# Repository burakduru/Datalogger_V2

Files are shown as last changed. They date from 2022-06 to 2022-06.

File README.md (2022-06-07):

# Datalogger_V2
    

__Ce répertoire Github regroupe la partie électronique et informatique embarquée de la carte d'acquistion Datalogger_V2 rédigé par Burak DURU en tant qu'apprenti ingénieur en électronique à la [Division Technique de l'INSU Meudon](https://www.dt.insu.cnrs.fr/).__

## Carte d'acquisition 

Réalisation et mise en œuvre d'une carte d'acquisition avec un microcontrôleur [Teensy 3.6](https://www.pjrc.com/store/teensy36.html) dans le but de recevoir/traiter des valeurs de thermistances/résistances chauffantes et transmettre/reçevoir des informations via plusieurs mode de communications

Fonctionnalités de la carte d’acquisition :
* Microcontrôleur [Teensy 3.6](https://www.pjrc.com/store/teensy36.html) :
  * Processeur 32 bits: Cortex-M4 @ 180 MHz 
  * Mémoires: 1M Flash, 256K RAM et 4K EEPROM
  * Microcontrôleur MK66FX1M0VMD18
  * Port USB High Speed (480 Mbit/sec)
  * 2 port Bus CAN
  * 22 sorties PWM
  * 4 ports I2C
  * 62 broches E/S (dont 48 format DIL compatible breadboard - non tolérante au +5 V). Les entrées/sorties fonctionnent en 3.3 V 
  * 25 entrées analogiques (à 2 ADC résolution 13 bits)
  * 2 sorties analogiques (DAC résolution 12 bits)
  * Port USB Full Speed (12 Mbit/sec)
  * Ethernet jusqu'à 100 Mbits/sec
  * Port intégré (4-bit SDIO) pour carte microSD™ (carte non livrée)
  * Port Audio numérique I2S, 4 canaux Entrée & Sortie
  * 14 Timers Hardware
  * 3 ports SPI (dont 1 avec FIFO)
  * 6 port série (dont 2 FIFO et Baud Rates rapides)
  * Horloge temps réelle
  * Dimensions: 62,3 x 18 x 4,2 mm

  teensy3 6
 
* [Socket MikroBUS](https://www.mikroe.com/mikrobus/) pour l’utilisation des modules “Click”
* Ethernet ([Module WIZ820-IO](https://www.wiznet.io/product-item/wiz820io/))
* Sortie DAC, GPIO et commande Interlock Laser
* Bus CAN
* Liaison RS232
* Connectique pour le réseau de thermistances/tensions
* Alimentation externe
* Relais

datalogger_v2_3D

## Programmes utilisés

* __[Datalogger](https://github.com/burakduru/dataloggerv2/blob/main/Programmes/microdial_datalogger_V2/microdial_datalogger_V2.ino)__ : *Permettant de récupérer les informations de températures et de tensions des connectiques thermistances YSI[...] et de tensions V[...] via une transmission RS232*  
* __[Bus CAN](https://github.com/burakduru/dataloggerv2/blob/main/Programmes/bus_can/bus_can.ino)__ : *Permettant de recevoir/transmettre des trames de données depuis le bus de donnée CAN. (Dans notre exemple, transmission d’une donnée de compteur et de thermistances)*
* __[Ethernet](https://github.com/burakduru/dataloggerv2/blob/main/Programmes/wiz820io_mqtt_ethernet/wiz820io_mqtt_ethernet.ino)__ : *Programme d’exemples pour l’initialisation module Ethernet / Envoi et réception de trames UDP / Connexion à un broker MQTT et le statut de connexion* 
* __[Programmes de tests](https://github.com/burakduru/dataloggerv2/tree/main/Programmes/click_exemples)__ : *Modules “Click” utilisés*
* __[WIFI](https://github.com/burakduru/dataloggerv2/blob/main/Programmes/adafruitio_wifi/adafruit_io_wifi_mqtt_16_04.ino)__ : *Programme pour le scan/connexion des réseaux et connexion à un serveur/broker MQTT* 
* __[LoRa](https://github.com/burakduru/dataloggerv2/blob/main/Programmes/LoRa_microdial_send_temp/LoRa_microdial_send_temp.ino)__ : *Plusieurs programmes permettant d’initialiser et d’envoyer des trames de données via le protocol de communication bas débit LoRa* 
* __[AdafruitIO | ThinkSpeak](https://github.com/burakduru/dataloggerv2/tree/main/Programmes)__ : *Envoi/réception de données en utilisant une connexion Internet (via Ethernet ou WIFI) à un serveur MQTT* 

## Matériel

* __[PCB](https://github.com/burakduru/dataloggerv2/tree/main/PCB)__: *Fichiers schématique (.schDoc) et PCB (.pcbDoc) sous Altium Designer*

## Schéma fonctionnement complet

* __[Schématique](https://github.com/burakduru/dataloggerv2/blob/main/MicroDial_Data_Log_V2_SCH.pdf)__ : *Fichier PDF regroupant la schématique de la carte* d'acquisition Datalogger_V2

Guide d'utilisation 
===================

<!--ts-->
* [Installation de Teensyduino](#installation-de-teensyduino)    
* [Installation de bibliothèques sous Teensyduino](#installation-de-bibliothèques-sous-teensyduino)  
* [Modules Click Board](#modules-click-board)
* [Pinout DataloggerV2](#pinout-dataloggerV2)
* [Liaison RS232](#liaison-rs232)
* [Visual Studio](#visual-studio) 
* [Bus CAN](#bus-can)  
* [Ethernet](#ethernet)  
* [WIFI](#wifi)
* [AdafruitIO](#adafruitio) 
* [Thingspeak](#thingspeak)
* [LoRa](#lora)  
* [Bluetooth Low Energy](#bluetooth-low-energy)
<!--te-->

Installation de Teensyduino
---------------------------

Télécharger l’Add-On pour l’IDE d’Arduino en utilisant ce lien sous Windows: https://www.pjrc.com/teensy/td_download.html.
Avec Windows 10, il n’y a pas de driver à installer : On choisit donc, le chemin d’accès où se trouve arduino.exe : 

teensyduino1

Choisir comme type de carte sur Arduino :
Teensy 3.6 / USB Type : “Serial” / CPU Speed : “180MHz” / Port : “Numéro de Port du Teensy”

teensyduino2

Installation de bibliothèques sous Teensyduino
----------------------------------------------

Toutes les bibliothèques nécessaires à l’implémentation des programmes sont disponibles dans le fichier “Bibliothèques”. Copier-coller ces librairies dans les bibliothèques source de la carte Teensy :

biblitotheque_teensy

Programmes de tests : 
- Programme de test pour chacun des Click Board présentés
- LED RGB/ Relais/ DAC/ Bus CAN
- Programme de tests des thermistances/résistance chauffante (relevé de température et de tension)
- Plusieurs programmes pour tester la liaison RJ45 (Ethernet) (connexion à un broker MQTT/ UDP/ Webserver et l’état de l’ethernet)
- Test de la liaison WIFI Click Board (Vérification mise à jour firmware/ scan et connexion à des réseaux).
- Connection au broker MQTT IO.Adafruit et ThinkSpeak (Ethernet et WIFI)
- Envoi données de température en passant par le réseau LoRa (LoRa Click)
- Application sous Visual Studio afin de récupérer les valeurs de températures/tensions et contrôler les relais/led RGB et le DAC

Modules Click Board
-------------------

Liste des modules MikroElektronika testés et compatible avec la carte d'acquisition : 
- [GNSS 4 Click](https://www.mikroe.com/gnss-4-click/)
- [GNSS Click](https://www.mikroe.com/gnss-click/)
- [Temp-Hum 4 Click](https://www.mikroe.com/temp-hum-4-click/)
- [Air-Quality 4 Click](https://www.mikroe.com/air-quality-4-click/)
- [Oled-W/B Click](https://www.mikroe.com/oled-w-click/)
- [WIFI 7 Click](https://www.mikroe.com/wifi-7-click/)
- [CAN SPI Click](https://www.mikroe.com/can-spi-33v-click/)
- [BLE ⅔ Click](https://www.mikroe.com/ble-p-click/)
- [LoRa Click](https://www.mikroe.com/lr-click/)

Pinout DataloggerV2
-------------------

pinout_datalogger

Liaison RS232
-------------

Programme __[Datalogger](https://github.com/burakduru/dataloggerv2/blob/main/Programmes/microdial_datalogger_V2/microdial_datalogger_V2.ino)__ regroupé en plusieurs fonctions permettant la conversion d’une valeur analogique à numérique puis cette valeur en tension, de cette tension en une valeur de résistance puis en température. Finalement ces valeurs sont transmises via la liaison RS232 ci-dessous :

rs232

Visual Studio
-------------

Pour l’[utilisation](https://visualstudio.microsoft.com/fr/) de l’application Windows Forms “DataLoggerNMEA”, il faut tout d’abord implémenté le code “[interface_C_sharp.ino](https://github.com/burakduru/dataloggerv2/blob/main/Programmes/interface_C_sharp/interface_C_.ino)” dans la carte Data_Logger. L’envoi de la trame NMEA comportant les valeurs de températures des thermistances et de tensions se fait toutes les 5 secondes :

Pour la réception de données envoyées depuis l’application DataLoggerNMEA, le décodage est effectué par la fonction “decoder_message_operateur” et vérifié par “crc_check”.
Depuis le moniteur série, on peut confirmer la donnée reçu par la vérification de l’entête du message (exemple : #RELAIS;2;0 ce qui correspond à une commande d’état bas au relais n°2.) et l’envoi de la trame NMEA.

moniteur_serie

Interface de l'application :

visual_studio

Bus CAN
-------

Exemple d'application du bus CAN : Implémentation d’un code de transmission et de réception de trames de données en utilisant un identificateur pour chacune des cartes avec des données de température et de compteurs pour réaliser des tests  

datalogger_buscan_1

datalogger_buscan



Nous avons ici implémenté le code “[bus_can.ino](https://github.com/burakduru/dataloggerv2/blob/main/Programmes/bus_can/bus_can.ino)” pour la carte Data_Logger et “[can_teensy4_1.ino](https://github.com/burakduru/dataloggerv2/blob/main/Programmes/can_teensy4_1/can_teensy4_1.ino)” pour la Teensy 4.1. Lorsque l’on observe le signal CAN_H/CAN_L à l’oscilloscope, on constate deux trames de données. La première trame correspond à l’envoi depuis la carte Data_Logger et la seconde à l’envoi depuis la Teensy 4.1. On peut identifier ces 2 trames par leur ID, “0x7DF” et “0x7E8”. Pour la trame “0x7DF”, data[0] correspond à une donnée de température et data[1..7] correspond à  “2” à “8” en ASCII. Les 4 derniers octets correspondent au CRC (“cyclic redundancy check”).
Pour la trame “0x7E8”, data[0..5] correspond à la donnée recopiée à la réception de “0x7DF” et data[6..7] correspondent à des compteurs qui s’incrémentent à chaque envoi de données.

Ethernet
--------

Installation de la librairie Ethernet :
* Librairie disponible lors de l'installation de Teensyduino  
* Avec la Teensy 3.6 : 2 ports SPI matériels disponible pour notre cas, WIZNET est connecté à SPI1. Pour le bon fonctionnement du module WIZNET, il faut récupérer le fichier "[Ethernet](https://github.com/burakduru/dataloggerv2/blob/main/Libraries%20Altium/Ethernet.zip)" et le copier-coller ici :  

ethernet

Initialisation du module WIZNET :
* Le code ci-dessous permet de réinitialiser le WIZNET :

code_wiznet

* Fixer une adresse MAC et une adresse IP pour un réseau local en utilisant la fonction begin

adresse_mac

Programmes d'exemples disponibles : 
* __[wiz820io_linkstatus](https://github.com/burakduru/dataloggerv2/blob/main/Programmes/wiz820io_linkstatus/wiz820io_linkstatus.ino)__ : *Confirmation connexion Ethernet*
* __[wiz820io_mqtt_ethernet](https://github.com/burakduru/dataloggerv2/blob/main/Programmes/wiz820io_mqtt_ethernet/wiz820io_mqtt_ethernet.ino)__ : *Exemple connexion serveur MQTT adafruit.io*
* __[wiz820io_udp_send_receive](https://github.com/burakduru/dataloggerv2/blob/main/Programmes/wiz820io_udp_send_receive/wiz820io_udp_send_receive.ino)__ : *Envoi/Réception trames UDP via Hercules*
* __[wiz820io_webserver](https://github.com/burakduru/dataloggerv2/blob/main/Programmes/wiz820io_webserver/wiz820io_webserver.ino)__ : *Création d’un serveur WEB qui renvoi des valeurs des pins analogiques*

WIFI 
----

Utilisation du module [ATWINC1510](https://www.mikroe.com/wifi-7-click/) :
* Installation de la bibliothèque du module ATWINC1510 depuis le gestionnaire de bibliothèque

atwinc1510

* Vérification de la version du firmware en compilant le programme "__[CheckWifi101FirmwareVersion.ino](https://github.com/burakduru/dataloggerv2/blob/main/Programmes/wifi_7click_checkwifi_FirmwareVersion/CheckWifi101FirmwareVersion.ino)"__
* Installation du firmware WIFI depuis Arduino :

firmware_wifi

* Scan des différents réseaux disponibles en compilant le programme  "__[ScanNetworksAdvanced.ino](https://github.com/burakduru/dataloggerv2/blob/main/Programmes/wifi_7click_scanNetworks/ScanNetworksAdvanced.ino)__"

scan_wifi

On obtient ici plusieurs informations concernant les réseaux :
- Nom du réseau (SSID)
- Amplitude du signal en dBm
- Channel disponible 
- Protocol de chiffrement 

* Connexion à un réseau WIFI WPA en compilant le programme "__[ConnectWithWPA.ino](https://github.com/burakduru/dataloggerv2/blob/main/Programmes/wifi_7click_connectWPA/ConnectWithWPA.ino)__"
Ouvrir tout d’abord “arduino_secrets.h” puis définir le nom du réseau (secret_ssid) puis le mot de passe (secret_pass)  
Compiler finalement le programme le programme : si la connection est bien effectué, on obtient plusieurs information dont une adresse IP attribuée automatiquement au module  

* Connexion au broker MQTT IO.Adafruit via une connexion WIFI en compilant le programme "__[adafruitio_wifi.ino](https://github.com/burakduru/dataloggerv2/blob/main/Programmes/adafruitio_wifi/adafruit_io_wifi_mqtt_16_04.ino)__"

AdafruitIO
----------

[AdafruitIO](https://io.adafruit.com/) est une plateforme IoT qui propose un service cloud permettant à la fois d’afficher/d’envoyer des informations sur une interface web avec une affichage en temps réels de données comme par exemple le contrôle de relais/LEDs pour notre cas

Utilisation d'IO.Adafruit.com :

* Création d’un compte adafruitIO sur https://io.adafruit.com
* Récupération à partir de l’interface “My Key” de l’username et de l’active key

ioadafruit

* Utilisation du programme d’exemple IOAdafruit : Contrôle des relais / led et affichage d’une température 
Avant l'utilisation, remplacer la bibliothèque : __8. Ethernet__   
Puis, ajout des bibliothèques AdafruitIO : (dossier “Bibliothèques” sinon “Adafruit IO Arduino” dans le gestionnaire de bibliothèque)

biblitotheque_adafruit

__Architecture du broker MQTT AdafruitIO :__  

broker_mqtt

* Température comme data et io.adafruit.com comme MQTT-Broker
* Données de températures acquise par la carte Teensy
* Envoi de data depuis la Teensy vers le broker MQTT en utilisant la bibliothèque Ethernet du module WIZ820-IO et AdafruitMQTT pour publier/souscrire

__Dashboard IO.Adafruit pour gérer/revoir les informations de la carte d'acquisition :__  

Pour comprendre la création/utilisation du dashboard IO.Adafruit se référer aux slides 21 et 22 du guide d'utilisation *"[MicroDial_Data_Logger_V2.pdf](https://github.com/burakduru/dataloggerv2/blob/main/MicroDial_Data_Log_V2_SCH.pdf)"*  

dashboard_adafruitio

Thingspeak
----------

[Thingspeak](https://thingspeak.com/) est une plateforme IoT semblable à IO.Adafruit :  
* Création d’un compte Thingpseak via thingspeak.com  
* Création d’un channel afin d’afficher sur un dashboard les “fields” :

channel_thingspeak

* Récupération du Channel ID et de l’API Key pour une connexion à la plateforme 

thingspeak_lora

LoRa
----

Protocole de télécommunication LoRa bas débit et à faible consommation électrique :

lorawan

La transmission LoRa est constitué de plusieurs étapes : 
* Configuration du transceiver RN2483 (LoRa Click) en utilisation la bibliothèque “rn2483”
* Communication RF à 868.5MHz entre le module Click LoRa et le Gateway LoRa de la DT
* Depuis le Gateway connection à Internet puis au serveur TTN (The ThingsNetwork)
* Configuration de TTN afin d’enregistrer le device et de recevoir/envoyer les trames entre les différents modules LoRa et le gateway
* Configuration depuis TTN vers un broker MQTT (ThingSpeak) afin d’afficher par exemple la courbe de la température

Configuration du Gateway Dragino LPS8 : 
* Cette passerelle multi-channel permet de relier le réseau sans fil LoRa(868 MHz) à un réseau IP via une connexion WiFi ou Ethernet

LoRa_1

* Pour la configuration du gateway, nous disposons de plusieurs possibilités de connexion. Soit une connexion à Internet via un réseau WIFI et une connection LAN du PC vers le Gateway (RJ45) sinon une connexion à Internet via le port WAN (RJ45) et une connexion entre le PC et le gateway en se connectant au réseau WIFI du gateway (dragino-1f….)
* Connexion WIFI à Internet et LAN pour configurer le gateway (adresse 10.130.1.1)  : username : root / password : dragino
* Cliquer sur “LoRaWAN” puis choisir comme Service Provider “The Things Network” et comme Server Adress le serveur européen “TTN-routeur-EU, EU 433 and EU 863-870”.

LoRa_2

* Se rendre sur “Network” puis “WIFI”, cochez enable WiFi WAN Client puis entrer le nom du réseau WIFI “Host WiFi SSID”, le mot de passe du réseau “Passphrase” et enfin choisir depuis WIFI Survey le nom du réseau puis le type de cryptage. Finalement, la connexion est validée en dessous

LoRa_3

* Après avoir connecté le Gateway à Internet, vérifions la connection au serveur TTN. Pour cela, il faut se rendre dans “home”

LoRa_4

* Avant de configurer le gateway sur TTN, il faut récupérer le gateway ID. Se rendre sur “LoRaWAN” puis dans “LoRaWAN Configuration” et recopier le Gateway ID

LoRa_5

* Se connecter à “thethingsnetwork.org”, puis dans “profil” cliquer sur “Console”. Choisir “Gateway” puis “register gateway”. Entrer le Gateway ID précédemment copié, choisir Europe pour Frequency Plan et Indoor pour Antenna Placement

LoRa_6

Impact du faceur d'étalement sur la portée et le débit (SF - Spreading Factor)

LoRa_7

Bluetooth Low Energy
--------------------------

[BLE P Click](https://www.mikroe.com/ble-p-click) :
* Puce Bluetooth Low Energy (BLE) nRF8001 
* Bus SPI (via le socket MikroBUS)
* Utilisation de bibliothèque open source Arduino => utilisation du module BLE
* Connection avec un smartphone en bluetooth via l’application Bluefruit Connect) 
* Envoi informations de températures et tensions en bluetooth 

ble_click

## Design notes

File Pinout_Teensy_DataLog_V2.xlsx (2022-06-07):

PINOUT MICRODIAL_DATA_LOG_V2 |  |  |  | MikroBUS Host Socket |  |  |  | WIZ820io |  |  |  | MODE ALIMENTATION CARTE MICRODIAL_DATA_LOG V2
TEENSY 3.6 |  |  |  | MKB_SK1 |  |  |  | ETHERNET |  |  |  | ONLY USB
CÔTE GAUCHE |  |  | CÔTE DROIT | CÔTE GAUCHE |  | CÔTE DROIT |  | CÔTE GAUCHE |  | CÔTE DROIT |  | JP1 | JP2 | JP3 | JP4 | Remarque
SIGNAL | PIN |  | SIGNAL | SIGNAL | PIN |  | SIGNAL | SIGNAL | PIN |  | SIGNAL | ON | OFF | OFF | OFF | Alimentation par Carte Teensy via USB (Mode Débug et programmation)
GND |  |  | VIN_T | A0_CLICK | 1 | 16 | PWM_CLICK | GND | 1 | 1 | GND |  |  |  |  | Transmission via USB ou RS-232 selon programmation via JP1 (Fermé =USB, Ouvert = RS232)
SPI_MOSI1_WIZ | 0 |  | GND | RESET_CLICK | 2 | 15 | INT_CLICK | GND | 2 | 2 | 3.3V | External Power Supply with LDO_TEENSY_Supply_3.3V and USB disconnected or electric wire for transmission by USB
SPI_MISO1_WIZ | 1 |  | 3.3V_T | /CS_CLICK | 3 | 14 | RX_CLICK | SPI_MOSI1_WIZ | 3 | 3 | 3.3V | ON | OFF | ON | OFF | Alimentation via PWR_IN < 5.6V et LDO du TEENSY 3.3V (LP3861)
PWM_CLICK | 2 | 23 | SEL_C | SPI_SCK0 | 4 | 13 | TX_CLICK | SPI_SCK1_WIZ | 4 | 4 | PWDN_WIZ |  |  |  |  | Ne pas connecter USB pour la transmission RS-232 ou bien couper Fils sur Teensy 3.3V pour la transmission via USB
CAN0TX_MCP | 3 | 22 | SEL_B | SPI_MISO0 | 5 | 12 | SCL1_CLICK | /CS1_WIZ820io | 5 | 5 | /RESET_WIZ |  |  |  |  | Transmission via USB ou RS-232 selon programmation via JP1 (Fermé =USB, Ouvert = RS232)
CAN0RX_MCP | 4 | 21 | SEL_A | SPI_MOSI0 | 6 | 11 | SDA1_CLICK | /INT_WIZ | 6 | 6 | SPI_MISO1_WIZ | External Power Input Supply and Internal Power Supply (3.3V)
CMD_RESET_RELAIS_2 | 5 | 20 | Sel_Monitor | 3.3V | 7 | 10 (NC) | 5V |  |  |  |  | OFF | ON | ON | ON | Alimentation via PWR_IN < 5.6V et LDO_Externe (TPSM84203AB)
CMD_SET_RELAIS_2 | 6 | 19 | /INVALID | GND | 8 | 9 | GND |  |  |  |  |  |  |  |  | Ne pas connecter USB pour la transmission RS-232 ou bien couper Fils sur Teensy 3.3V pour la transmission via USB
RX_CLICK | 7 | 18 | /SHDN_MAX3227 |  |  |  |  |  |  |  |  |  |  |  |  | Transmission via USB ou RS-232 selon programmation via JP1 (Fermé =USB, Ouvert = RS232)
TX_CLICK | 8 | 17 | 17/A3/PWM/SDA0/Touch
/CS_CLICK | 9 | 16 | CMD_RELAIS_1
/CS_ADS8344E | 10 | 15 | IO_INTERLOCK_LASER
SPI_MOSI0 | 11 | 14 | A0_CLICK
SPI_MISO0 | 12 | 13 | SPI_SCK0
3.3V_T |  |  | GND
GPIO0_SMA | 24 | A22 | DAC1
GPIO1_SMA | 25 | A21 | DAC0
PWDN_WIZ | 26 | 39 | /RESET_WIZ
RESET_CLICK | 27 | 38 | SDA1_CLICK
INT_CLICK | 28 | 37 | SCL1_CLICK
LED_RGB_ROUGE | 29 | 36 | /INT_WIZ
LED_RGB_BLEU | 30 | 35 | LED_RGB_VERT
CS1_WIZ820io | 31 | 34 | RXD
SPI_SCK1_WIZ | 32 | 33 | TXD

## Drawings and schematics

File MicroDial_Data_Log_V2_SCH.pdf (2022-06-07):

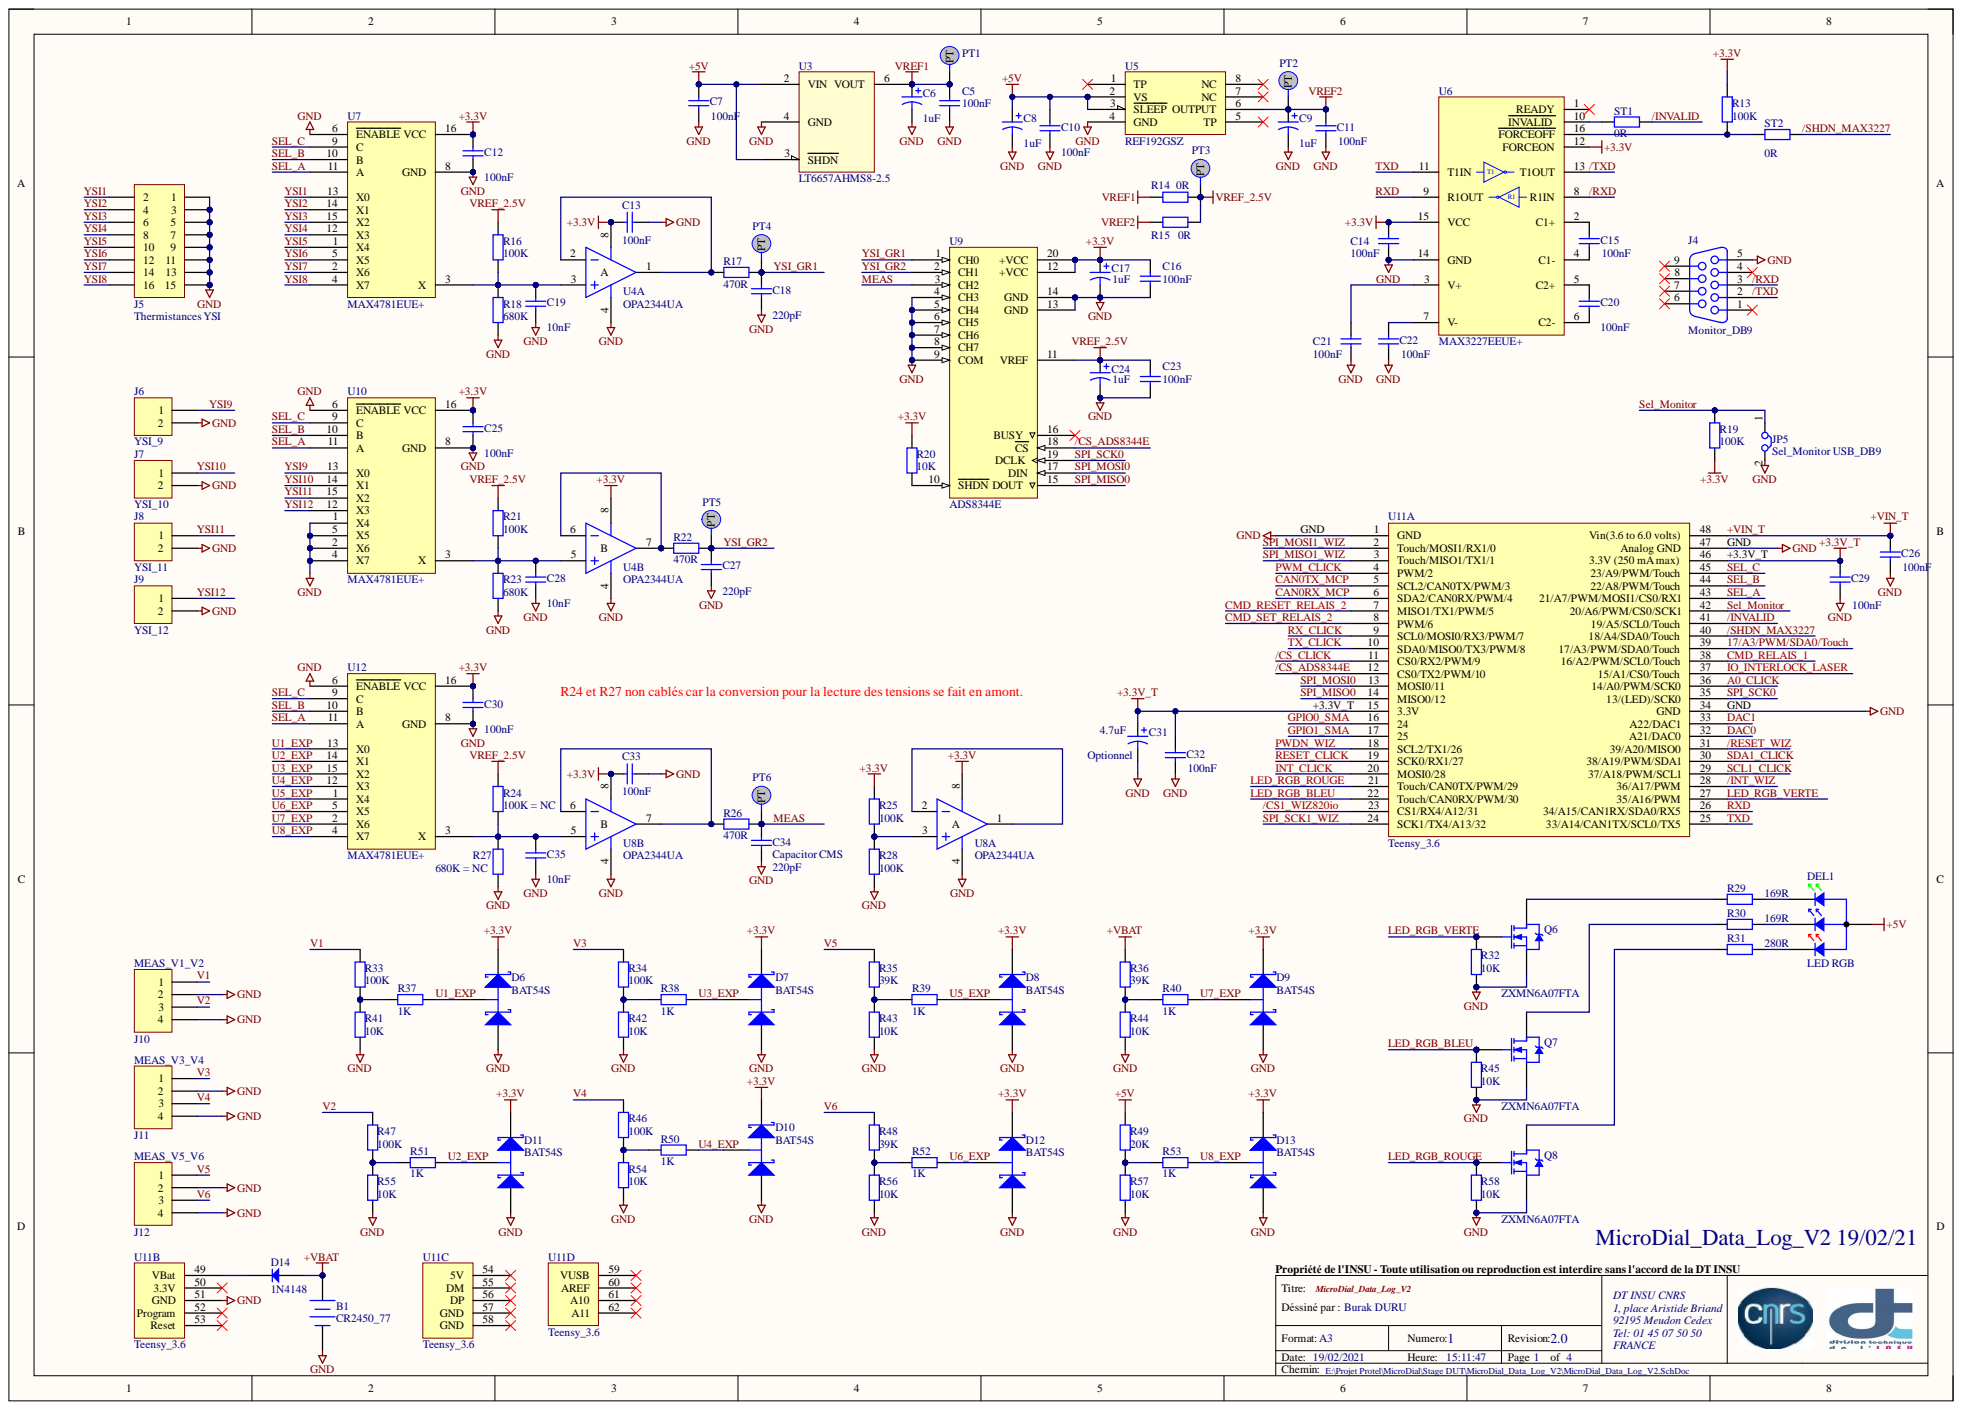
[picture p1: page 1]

R24 et R27 non cablés car la conversion pour la lecture destensions se fait en amont.

Propriété de l'INSU - Toute utilisation ou reproduction est interdire sans l'accord de la DT INSU
Titre:
Déssiné par : Burak DURU

E:\Projet Protel\MicroDial\Stage DUT\MicroDial_Data_Log_V2\MicroDial_Data_Log_V2.SchDoc

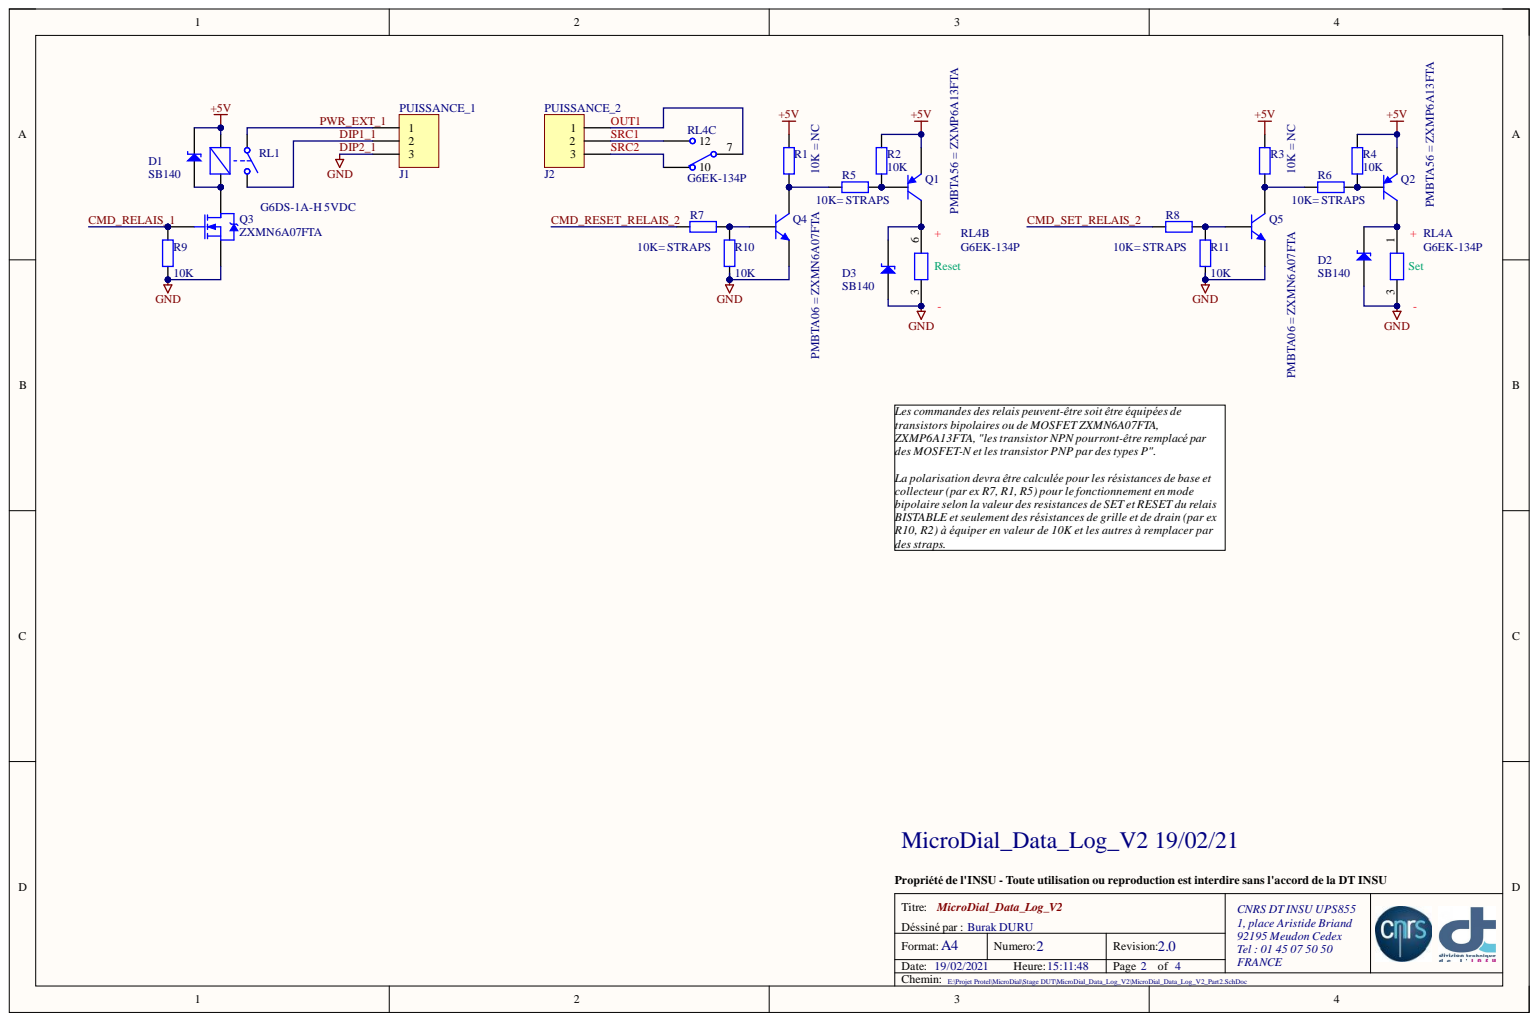
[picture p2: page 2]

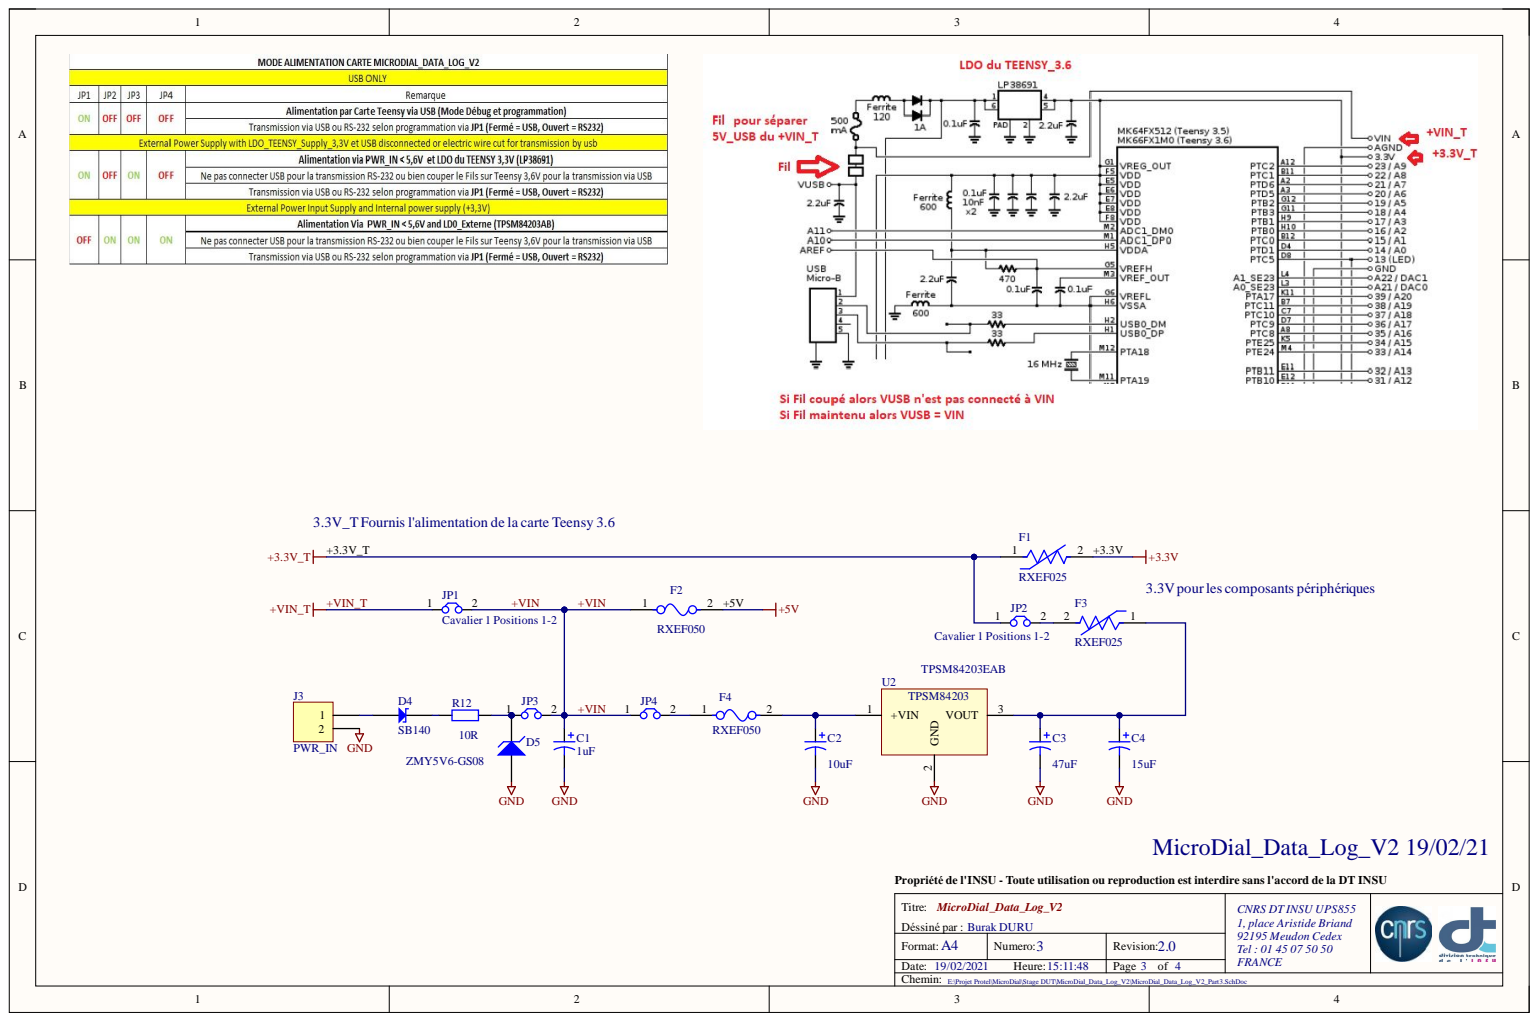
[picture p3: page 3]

3.3V_TFournis l'alimentation de la carte Teensy 3.6

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

Titre:
Déssiné par : Burak DURU

E:\Projet Protel\MicroDial\Stage DUT\MicroDial_Data_Log_V2\MicroDial_Data_Log_V2_Part3.SchDoc

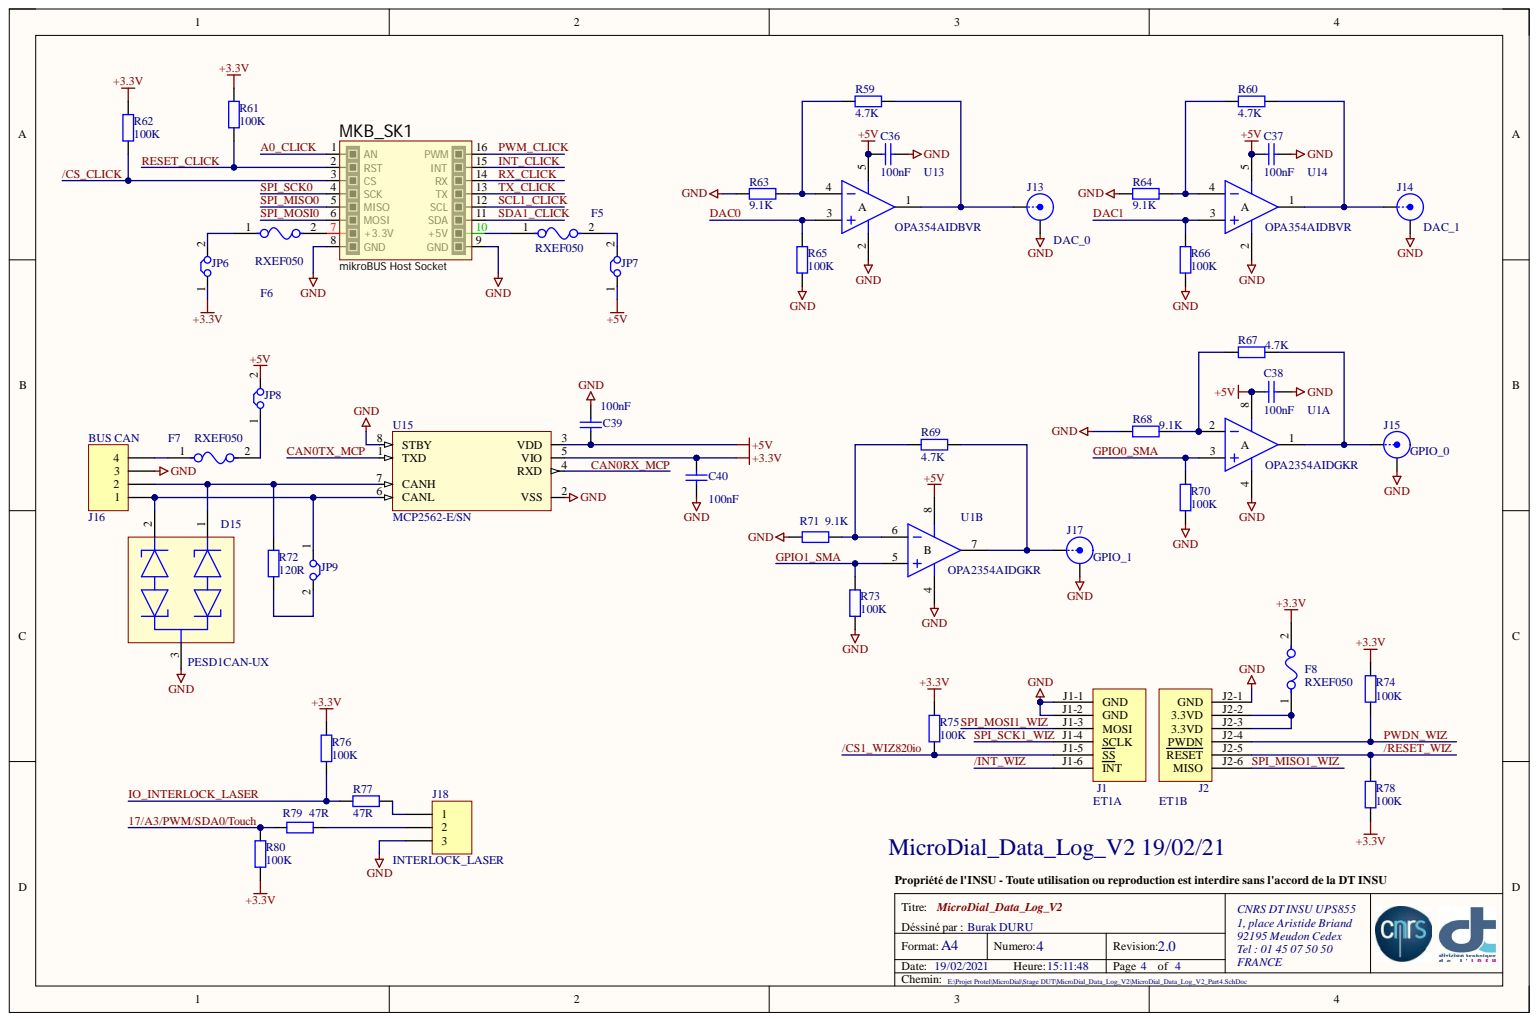
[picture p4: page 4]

CANL 6

D15 | MCP2562-E/SN 2

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

Titre:
Déssiné par : Burak DURU

E:\Projet Protel\MicroDial\Stage DUT\MicroDial_Data_Log_V2\MicroDial_Data_Log_V2_Part4.SchDoc

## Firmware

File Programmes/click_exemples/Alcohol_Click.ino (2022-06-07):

/************************************************************************
*                                                                                                                                        
*    Test du module "Alcohol Click"                                            
*                                                                    
*************************************************************************
* Description:  MIKROE-1586                                               
* La valeur du taux d'alcool est affiché sur le moniteur série et 
* sur le module bargraph.
*  
* Matériel
*        1. Arduino Uno                                       
*        2. Shield "Click" pour arduino UNO
*        3. Module "Alcohol Click" inséré sur le support N°1 du shield
*        4. Module "Bargraph Click" inséré sur le support N°2 du shield
*        
***********************************************************************/

 
// Affectation des broches du module Alcohol
#define AN A0                               // broche de sortie du module
// Affectation des broches du module Bargraph
#define SDIN 11    // broche DS des 74HC595
#define SCLK 13    // broche SHCP des 74HC595
#define LATCH 9   // broche STCP des 74HC595
#define DISPLAY 5  // broche de validation du bargraph

int valeur;
int led=15;
int MSB;
int LSB;

void setup()
{
Serial.begin(9600);                         // initialisation de la liaison série 
pinMode(SDIN, OUTPUT);
pinMode(SCLK, OUTPUT);
pinMode(LATCH, OUTPUT);
pinMode(DISPLAY, OUTPUT);
digitalWrite(DISPLAY,HIGH);                  // validation du bargraph
}

void loop()
{
valeur=0;
for(int i=0;i<10;i++)                       // acquisition de 10 échantillons
  {
    valeur= valeur+analogRead(AN);
    delay(10);
  }
valeur=valeur/10;                           // calcul de la valeur moyenne
// Gestion des led du bargraph
if (valeur<199)
{
  led=0;
}
if ((valeur>200)&&(valeur<283))
{
  led=1;
}
if ((valeur>284)&&(valeur<367))
{
  led=3;
}
if ((valeur>368)&&(valeur<451))
{
  led=7;
}
if ((valeur>452)&&(valeur<535))
{
  led=15;
}
if ((valeur>536)&&(valeur<619))
{
  led=31;
}
if ((valeur>620)&&(valeur<703))
{
  led=63;
}
if ((valeur>704)&&(valeur<787))
{
  led=127;
}
if ((valeur>788)&&(valeur<871))
{
  led=255;
}
if ((valeur>872)&&(valeur<955))
{
  led=511;
}
if (valeur>956)
{
  led=1023;
}
// Gestion du bargragh
LSB=led&0x00FF;                             // récupération des 8 bit de poids faibles de la variable i
MSB=led&0xFF00;                             // récupération des 8 bit de poids forts de la variable i
MSB=MSB>>8;                                 // décalage des 8 bits de poids forts pour les mettre au format octet
digitalWrite(LATCH, LOW);                   // blocage du registre de sortie des 74HC595
shiftOut(SDIN, SCLK, MSBFIRST, MSB);        // envoi des 8 bits de poids forts sur le second 74HC595
shiftOut(SDIN, SCLK, MSBFIRST, LSB);        // envoi des 8 bits de poids faibles sur le premier 74HC595
digitalWrite(LATCH, HIGH);                  // déblocage du registre de sortie des 74HC595
// Affichage
Serial.print("Valeur = ");            
Serial.println(valeur);
delay(1000);                                // pause entre deux mesures
}

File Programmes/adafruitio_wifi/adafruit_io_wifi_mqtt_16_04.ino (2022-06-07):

#include <SPI.h>
#include <WiFi101.h>
#include <PubSubClient.h>
#include <Ethernet.h>
#include <EthernetClient.h>

#define RST_click 27
#define INT_click 28
#define CS_click 9
#define PWM_click 2

char ssid[] = "iPhone";        // your network SSID (name)
char pass[] = "haciduru66";    // your network password (use for WPA, or use as key for WEP)
unsigned long int millis_last_publish = 0;
int status = WL_IDLE_STATUS;

EthernetClient client;
WiFiClient wificlient;
PubSubClient mqttclient(client);
int x = 2;
byte mac[] = {0x90, 0xA2, 0xDA, 0x10, 0x40, 0x4F};
IPAddress ip(192, 168, 0, 177);
IPAddress myDns(192, 168, 0, 1);
//// PERMET DE RESET LE TEENSY POUR SE RECONNECTER WIFI
#define RESTART_ADDR       0xE000ED0C
#define READ_RESTART()     (*(volatile uint32_t *)RESTART_ADDR)
#define WRITE_RESTART(val) ((*(volatile uint32_t *)RESTART_ADDR) = (val))

void setupioteensy()
{
  pinMode(16,OUTPUT); //setup relais1
  
}


void setupwifi(){
  int nb_tentative=0;
  Serial.println("VOUS ETES DANS LA FONCTION SETUP WIFI");
  pinMode(RST_click,OUTPUT);
  digitalWrite(RST_click, HIGH);
  digitalWrite(RST_click, LOW);
  delay(1000);
  digitalWrite(RST_click,HIGH);
  WiFi.setPins(CS_click,INT_click,RST_click,PWM_click);
  
  // attempt to connect to WiFi network:
  while (WiFi.status() != WL_CONNECTED && nb_tentative++<10 ) {
    Serial.print("Attempting to connect to SSID: ");
    Serial.println(ssid);
    // Connect to WPA/WPA2 network. Change this line if using open or WEP network:
    status = WiFi.begin(ssid, pass);
    
    // wait 10 seconds for connection:
    if(WiFi.status() != WL_CONNECTED) delay(1000);
  }
  Serial.println("Connected to wifi");
  Serial.println(WiFi.localIP());
}
void setup() {
  Serial.begin(115200);
  setupioteensy();
  setupwifi();
  Serial.println("function wifi OK");
  mqttclient.setServer("io.adafruit.com",1883);
  mqttclient.setCallback(callback);
  if (mqttclient.connect("io.adafruit.com", "burakduru", "aio_WUKY97uE23bJxuS8o4EiKMkpj6XH")){
    mqttclient.publish("burakduru/feeds/digital","1883");
    mqttclient.subscribe("burakduru/feeds/led");
    mqttclient.publish("burakduru/feeds/led/get",0); //grâce au get renvoi de la dernière valeur de relais1
  }
}

void loop() {
  char chaine[80];
  // put your main code here, to run repeatedly:
  if (!mqttclient.connected()) {
    if(WiFi.status() != WL_CONNECTED)
      setupwifi();
      Serial.println("LOOP 105");
      reconnect();
    if(mqttclient.connected())
    {
      mqttclient.subscribe("burakduru/feeds/led");
      //mqttclient.publish("burakduru/feeds/led/get",0); //grâce au get renvoi de la dernière valeur de relais1
    }
    else
    delay(1000);  
  }
  if((millis()-millis_last_publish)>2999) //publish toute les 3 secondes 
  {
    sprintf(chaine,"%d",x++);
    millis_last_publish =millis();
    mqttclient.publish("burakduru/feeds/digital",chaine);
    }
  /*mqttclient.subscribe("burakduru/feeds/led");
  delay(1000);*/
  mqttclient.loop();
}

void reconnect() {
  // Loop until we're reconnected
  while (!mqttclient.connected()) {
    if(WiFi.status() != WL_CONNECTED)
    {
      setupwifi();
      WRITE_RESTART(0x5FA0004);
      delay(1000); 
    }
    else 
    {
      Serial.print("Attempting MQTT connection...");
      // Attempt to connect
      if (mqttclient.connect("teensyclient", "burakduru", "aio_WUKY97uE23bJxuS8o4EiKMkpj6XH")) {
        Serial.println("connected");
      } else {
      Serial.print("failed, rc=");
      Serial.print(mqttclient.state());
      Serial.println(" try again in 5 seconds");
      // Wait 5 seconds before retrying
      delay(5000);
      }
    }
  }
}

void callback(char* topic, byte* payload, unsigned int length) {
 
  Serial.print("Message arrived in topic: ");
  Serial.println(topic);
  int relay=0; 
  Serial.print("Message:");
  for (int i = 0; i < length; i++) {
    Serial.print((char)payload[i]);
    if((char)payload[i] == '0')
    {
      relay=0;
      Serial.println("OK DOGECOIN");
      digitalWrite(16,0);
    }
    if((char)payload[i] == '1')
    {
      relay=1;
      Serial.println("OK TO THE MOON");
      digitalWrite(16,1);
    }
  }
  //digitalWrite(16,relay);
  Serial.println();
  Serial.println("-----------------------");
 
}

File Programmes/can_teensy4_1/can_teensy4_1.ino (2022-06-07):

/*
* Demo sketch for use with:
* http://skpang.co.uk/catalog/teensy-41-triple-can-board-with-240x240-ips-lcd-p-1592.html
* 
* can1 baudrate 500kbps
*
* can2 baudrate 500kbps
*
* can3 baudrate 
* Nominal baudrate 500kbps
* CAN FD data baudrate 2000kbps
*
* www.skpang.co.uk May 2020
*
*
* */

#include <FlexCAN_T4.h>

FlexCAN_T4FD<CAN3, RX_SIZE_256, TX_SIZE_16> FD;
FlexCAN_T4<CAN2, RX_SIZE_256, TX_SIZE_16> can2;
FlexCAN_T4<CAN1, RX_SIZE_256, TX_SIZE_16> can1;

#include <SPI.h>
#include <ST7735_t3.h> // Hardware-specific library
#include <ST7789_t3.h> // Hardware-specific library
#include <ST7735_t3_font_Arial.h>

#define TFT_RST    32   // chip reset
#define TFT_DC     9   // tells the display if you're sending data (D) or commands (C)   --> WR pin on TFT
#define TFT_MOSI   11  // Data out    (SPI standard)
#define TFT_SCLK   13  // Clock out   (SPI standard)
#define TFT_CS     10  // chip select (SPI standard)
 
int LCD_BL = 33;       // LCD back light control

ST7789_t3 tft = ST7789_t3(TFT_CS, TFT_DC, TFT_MOSI, TFT_SCLK, TFT_RST);

IntervalTimer timer;
uint8_t d=0;
bool stopfd = 0;

void canSniff20(const CAN_message_t &msg) { // global callback

  Serial.print("T4: ");
  Serial.print("MB "); Serial.print(msg.mb);
  Serial.print(" OVERRUN: "); Serial.print(msg.flags.overrun);
  Serial.print(" BUS "); Serial.print(msg.bus);
  Serial.print(" LEN: "); Serial.print(msg.len);
  Serial.print(" EXT: "); Serial.print(msg.flags.extended);
  Serial.print(" REMOTE: "); Serial.print(msg.flags.remote);
  Serial.print(" TS: "); Serial.print(msg.timestamp);
  Serial.print(" ID: "); Serial.print(msg.id, HEX);
  Serial.print(" IDHIT: "); Serial.print(msg.idhit);
  Serial.print(" Buffer: ");
  
  for ( uint8_t i = 0; i < msg.len; i++ ) {
    Serial.print(msg.buf[i], HEX); Serial.print(" ");
  } Serial.println();
}

void setup(void) {
  pinMode(LCD_BL, OUTPUT);
  digitalWrite(LCD_BL, HIGH);  // Turn LCD backlight on
  Serial.begin(115200); delay(1000);
  Serial.println("Teensy 4.0 CAN FD test. www.skpang.co.uk Jan 2020");
  FD.begin();
  
  CANFD_timings_t config;
  config.clock = CLK_24MHz;
  config.baudrate =   500000;
  config.baudrateFD = 2000000;
  config.propdelay = 190;
  config.bus_length = 1;
  config.sample = 75;

  FD.setRegions(64);
  FD.setBaudRate(config);
  FD.onReceive(canSniff);
  FD.setMBFilter(ACCEPT_ALL);
  FD.setMBFilter(MB13, 0x1);
  FD.setMBFilter(MB12, 0x1, 0x3);
  FD.setMBFilterRange(MB8, 0x1, 0x04);
  FD.enableMBInterrupt(MB8);
  FD.enableMBInterrupt(MB12);
  FD.enableMBInterrupt(MB13);
  FD.enhanceFilter(MB8);
  FD.enhanceFilter(MB10);
  FD.distribute();
  FD.mailboxStatus();

  can2.begin();
  can2.setBaudRate(500000);
  can2.setMBFilter(ACCEPT_ALL);
  can2.distribute();
  can2.mailboxStatus();

  can1.begin();
  can1.setBaudRate(500000);
  can1.setMBFilter(ACCEPT_ALL);
  can1.distribute();
  can1.mailboxStatus();
 
  tft.init(240, 240);
  tft.setRotation(0);
  tft.fillScreen(ST77XX_BLUE);
  tft.setCursor(5,5);
  tft.setTextColor(ST77XX_YELLOW);
  tft.setFont(Arial_32);
  tft.println("Teensy  4.1");
  tft.setCursor(10,80);
  tft.setFont(Arial_40 );
  tft.println("240x240");
  tft.setCursor(10 ,140);
  tft.println("IPS LCD");
  tft.setFont(Arial_16 );
  tft.setCursor(10,212);
  tft.println("www.skpang.co.uk");  

// timer.begin(sendframe, 500000); // Send frame every 500ms
}

void sendframe()
{
  CAN_message_t msg2;
  msg2.id = 0x40;

  for ( uint8_t i = 0; i < 8; i++ ) {
    msg2.buf[i] = i + 1;
  }

  msg2.buf[0] = d++;
  msg2.seq = 1;
  can2.write(MB15, msg2);

  CAN_message_t msg1;
  msg1.id = 0x7df;
  msg1.buf[0] = d;
  can1.write(msg1);

  CANFD_message_t msg;
  msg.len = 64;
  msg.id = 0x321;
  msg.seq = 1;
  msg.buf[0] = d; msg.buf[1] = 2; msg.buf[2] = 3; msg.buf[3] = 4;
  msg.buf[4] = 5; msg.buf[5] = 6; msg.buf[6] = 9; msg.buf[7] = 9;
  FD.write( msg);
}

unsigned char compteur_buffer_3=0;
unsigned char  compteur_buffer_4=0;

void loop() {
  FD.events(); /* needed for sequential frame transmit and callback queues */
  CANFD_message_t msg;
  CAN_message_t msgcan1;
  CAN_message_t msgcan2;

  if(FD.readMB(msg)){   /* check if we received a CAN frame */
      Serial.print("MB: "); Serial.print(msg.mb);
      Serial.print("  OVERRUN: "); Serial.print(msg.flags.overrun);
      Serial.print("  ID: 0x"); Serial.print(msg.id, HEX );
      Serial.print("  EXT: "); Serial.print(msg.flags.extended );
      Serial.print("  LEN: "); Serial.print(msg.len);
      Serial.print("  BRS: "); Serial.print(msg.brs);
      Serial.print(" DATA: ");
      for ( uint8_t i = 0; i <msg.len ; i++ ) {
        Serial.print(msg.buf[i]); Serial.print(" ");
      }
      Serial.print("  TS: "); Serial.println(msg.timestamp);
  }

  if(can1.read(msgcan1))
  {   /* check if we received a CAN frame */
      Serial.println("Got can1");
      Serial.print("MB: "); Serial.print(msgcan1.mb);
      Serial.print("  OVERRUN: "); Serial.print(msgcan1.flags.overrun);
      Serial.print("  ID: 0x"); Serial.print(msgcan1.id, HEX );
      Serial.print("  EXT: "); Serial.print(msgcan1.flags.extended );
      Serial.print("  LEN: "); Serial.print(msgcan1.len);
      Serial.print(" DATA: ");

      for ( uint8_t i = 0; i <msgcan1.len ; i++ ) {
        Serial.print(msgcan1.buf[i]); Serial.print(" ");
      }
      Serial.print("  TS: "); Serial.println(msgcan1.timestamp);
  }

#define PID_REPLY      0x7E8
  if(can2.read(msgcan2))
  {   /* check if we received a CAN frame */
    if(msgcan2.id == 0x7DF)
    {
       CAN_message_t msg2;
        msg2.id = PID_REPLY;
        msg2.len = 8;
        msg2.buf[0] = msgcan2.buf[0];
        msg2.buf[1] = msgcan2.buf[1];
        msg2.buf[2] = msgcan2.buf[2];
        msg2.buf[3] = msgcan2.buf[3];
        msg2.buf[4] = msgcan2.buf[4];
        msg2.buf[5] = msgcan2.buf[5];
        msg2.buf[6] = compteur_buffer_3++;
        msg2.buf[7] = compteur_buffer_4++;
        msg2.seq = 1;
        can2.write(msg2);
    }
      Serial.println("Got can2");
      Serial.print("MB: "); Serial.print(msgcan2.mb);
      Serial.print("  OVERRUN: "); Serial.print(msgcan2.flags.overrun);
      Serial.print("  ID: 0x"); Serial.print(msgcan2.id, HEX );
      Serial.print("  EXT: "); Serial.print(msgcan2.flags.extended );
      Serial.print("  LEN: "); Serial.print(msgcan2.len);
      Serial.print(" DATA: ");

      for ( uint8_t i = 0; i <msgcan2.len ; i++ ) {
        Serial.print(msgcan2.buf[i]); Serial.print(" ");
      }
      Serial.print("  TS: "); Serial.println(msgcan2.timestamp);
  }
}

void canSniff(const CANFD_message_t &msg) {
  if ( stopfd ) return;
  Serial.print("ISR - MB "); Serial.print(msg.mb);
  Serial.print("  OVERRUN: "); Serial.print(msg.flags.overrun);
  Serial.print("  LEN: "); Serial.print(msg.len);
  Serial.print(" EXT: "); Serial.print(msg.flags.extended);
  Serial.print(" TS: "); Serial.print(msg.timestamp);
  Serial.print(" ID: "); Serial.print(msg.id, HEX);
  Serial.print(" Buffer: ");
  
  for ( uint8_t i = 0; i < msg.len; i++ ) {
    Serial.print(msg.buf[i], HEX); Serial.print(" ");
  } Serial.println();
}
